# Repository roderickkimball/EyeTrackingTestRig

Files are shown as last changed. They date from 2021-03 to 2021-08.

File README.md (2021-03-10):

The Eye Tracker Test Rig is a robotic device that utilizes a set of artificial eyes and an artificial face to both manually and autonomously control a Surface Laptop via interface with a remote eye tracker. The rig features 3-axes of translational motion and 2-axes of rotational motion. The combination of these axes is intended to provide human-like motion for the artificial eyes and face. The rig is controlled via an Arduino Mega and features manual control via an Xbox controller.

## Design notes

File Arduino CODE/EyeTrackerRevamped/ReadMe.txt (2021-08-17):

State Machine Summary:

•	Menu Mode - Idle state of the robot. Waits for commands from the API or serial communication to switch states or return the current state.
•	Robot Run - Runs the robot by moving the desired subsystem to the commanded position. The commanded position is decoded from the g-code that is sent from the API. 
		ge(float, float) - moves eyes; gs(float, float, float) - moves shoulder; gn(float, float, float) - moves neck
•	Eye Calibrate - State to calibrate the eye servos. Calibration of the eye servos is important for all 4 eye servos to know what the 90-degree straight forward position of the eyes is. All commanded angles are incremented/decremented from this 90-degree position.
•	Neck Calibrate - State to calibrate the neck steppers. Calibration of the neck steppers is important to save the position of the steppers at which the neck platform is completely level with the base plate.
•	Shoulder Calibrate - State to calibrate the shoulder steppers. Calibration process includes the shoulder steppers hitting their "zero" or "home" position limit switches. 

Class Structure Summary:

ROBOT.h

•	Robot Class: Class encapsulates the entire eye tracker robot, including the eye, neck and shoulder objects, along with members indicating the current state of the robot, transformation matrices that go from the center 
		of the left and right eye to the screen, and public member functions to run the different states of the robot and interface with the API. 

	Private Members: 
		robotState (StateMachineState): Enumeration object that stores the current state of the robot (refer StateMachineState enumeration in Function.h).
		robotEyes (Eyes object): Eyes class object encapsulating the eye subsystem.
		robotNeck (NeckClass object): NeckClass object that encapsulates the neck subsystem.
		robotShoulder (Shoulder object): Shoulder object that encapsulates the shoulder subsystem.
		screenDotPos (Matrix(4)): Matrix that denotes the coordinates of the desired gaze position for the eyes.
	
	Protected Members:
		gLS, gRS (Matrix(4,4)): Matrices that denote the transformation matrix that goes from the center of left and right eyes respectively to the center of the screen.

	Private Member Functions:

		char getSerialCommand(): Obtains a single character command from the Hardware Serial or the connection to the API by performing Serial.read().
			Returns the passed in character from the serial port. 

		void updateKinematicChain(): Recalculates gLS and gRS by pulling the inverse transformation matrices from the shoulder, neck and eyes. Refer GetInverse****Transformation() in Eyes.h, RobotNeck.h and Shoulder.h.

		void setRobotPosition(char command): Sets the desired subsystem to the commanded position. This function is called immediately after the g code is sent from the API or serial communication, and is responsible for decoding the rest of the 
			g command to determine which subsystem is to be moved. 
	
		void getRobotPosition(char command): Gets the current position of the desired subsystem. This function is called immediately after the p command is sent from the API or serial communication, and is responsible for decoding the rest of the
			p command to determine which subsystem's position is to be printed.

		void runMenuModeState(): Runs the MenuMode state, that essentially waits for a user input from the Serial terminal to change the state to a desired one. 
			References getSerialCommand(). If the command is m, then it prints the current state. If the command is s-(int), it changes the state to the enumerated integer passed in.

		void runRobotRunState(): Runs the Robot Run state, that essentially reads the commands set in from the serial port or API, decodes the g or p code that is sent is and subsequently calls setRobotPosition(char) or getRobotPosition(char).
			'm' returns the state to MenuMode.

		void runEyeCalibrationState(): References getSerialCommand() and passes in the character obtained into Eyes::CalibrateEyes(char) function. 
			'm' returns the state to MenuMode.

		void runShoulderCalibrationState(): References the Shoulder::HomeShoulder() function that zeroes all three stepper axes. 'm' returns the state to MenuMode.

		void runNeckCalibrationState(): References getSerialCommand() and passes the obtained character into the RobotNeck::CalibrateNeck(char) function. 'm' returns the state to MenuMode.

	Public Member Functions:

		void init(): Initialization function for the robot class object. Initializes the eyes, neck and shoulder objects encapsulated. Calls the read-from-EEPROM function in each of the class objects. Calls the updateKinematicChain() function
			to load all of the variable updates into the kinematic chain instance. 

		void SetState(int stateNumber): Sets the state of the robot to the enumerated value of the stateNumber integer. 

		int GetState(): Gets the current state of the robot and returns the integer value of the enumeration.

		void RunState(): Determines the state of the robot through a switch-case and calls the private member function corresponding to that state of the robot. 

EYESUBSYSTEM.h : 
The Eye Subsystem header file includes all the enumeration, variables, and the Eye Subsystem class. Details of each can be found below.
•	Enumerations: 
		EyeMotor: Symbolic names for denoting which motor is being individually controlled and calibrated. Used in eye calibration. 

•	Eyes Class: Class encapsulates the entire eye subsystem of the robot, with objects for the 4 servo motors and functionalities to calibrate the eyes and parallax the eyes on the screen. 

	Private Members: 
		xServoL, zServoL, xServoR, zServoR (Servo): Servo objects for the LeftX, LeftZ, RightX and RightZ servo motors. 
		lXCenter, lZCenter, rXCenter, rZCenter (long int): Center positions in microseconds for each of the servo motors. 
		lXmicroSecondsPerDegree, lZmicroSecondsPerDegree, rXmicroSecondsPerDegree, rZmicroSecondsPerDegree (float): Denotes the number of microseconds required to move the left/right eye servos one degree.
	
	Protected Members:
		    /*
      		T - will be the frame of reference located at the center of the top of the neck.
      		D - will be the frame of reference at the center of the eye mechanisms,
      		with Z up, X to the right and Y along the axis of the straight 90-degree eyes
	      	L - will be the left eye's frame of reference with the origin at the center of rotation
	        and is aligned with the D frame when the 90-degree angle is commanded
	        R - will be the right eye's frame of reference with the origin at the center of rotation
	        and is aligned with D frame when the 90-degree angle is commanded
		    */
		gTD, gDL, gDR (Matrix(4,4): Transformation matrices that go from one frame of reference to another given above.
		gLT, gRT (Matrix(4,4)): Inverse transformation matrices that go from the center of the left and right eyes to the top of the neck.

	Private Member Functions:
		void parallax(Matrix(4) leftDotPos, Matrix(4) rightDotPos): Commands the left and right X,Z servo motors to the desired position on the screen indicated by parameters. 
			Parameters: leftDotPos indicates the desired gaze position in the left eye’s frame of reference. rightDotPos indicates the desired gaze position in the right eye’s frame of reference.

	Public Member Functions:
		void init(): Initializes eye class object. Must be called anytime the class object is created. Attaches servo objects to corresponding pins. Defaults value for center positions. Writes servos to corresponding center positions.
			Provides transformation matrices with starting values.

		void ParallaxEyesToPos(Matrix(4) screenDotPos, Matrix(4,4) gLS, Matrix(4,4) gRS): Creates the gaze position coordinates in the left and right eye’s frame of reference using the dotPosition and inverse transformation matrix parameters.
			Parameters: screenDotPos matrix denotes the coordinates of the desired gaze position in the screen’s frame of reference.
				gLS denotes the TF matrix that goes from center of left eye to the center of screen. gRS is the same but for the right eye.

		void CalibrateEyes(char eyeCalCommand,  Matrix(4,4) gLS, Matrix(4,4) gRS): The aim of the calibration function is to make the 2 eyes point to a single point at the center of the screen. This is done by incrementing/decrementing the center positions of each servo motor by 1 microsecond. 
			Parameters: eyeCalCommand will either pass in ‘u’ for increment, ‘d’ for decrement and corresponding EyeMotor enumeration for changing calibration motor.

		void WriteEyeCalibrationVariablesToProm(): Writes the center positions of each servo motor to the predetermined address in the EEPROM (refer PromAddress enumeration in Function.h).

		void ReadEyeCalibrationVariablesFromProm(): Reads the center positions of each servo motor from the predetermined address in the EEPROM and stores it in the center position members in the class object.

		Matrix(4,4) GetInverseLeftEyeTransformation(), GetInverseRightEyeTransformation(): Gets the inverse transformation matrices for the left and right eyes in the eye subsystem. Referenced by Robot::updateKinematicChain().

NECKCLASS.h : 
The Neck class header file includes all the enumerations, variables and the RobotNeck class. Details of each can be found below:

•	Enumerations: 
		NeckMotor: Symbolic names for denoting which neck stepper motor is being individually controlled. Used in neck calibration.

•	Global Variables: 
		float knowStepperPos: This is used as the default or zero stepper position for all neck motors when the neck is parallel to the base. 
		float spoolRadius: Radius of the spool on stepper shafts.
		float spoolCircumference: Circumference of the spool
		float mmPerRevs: Length of thread released in each stepper revolution.
		float stepsPerRev: Number of steps for neck steppers in one revolution.
		float mmPerStep: Length of thread released in one stepper step.
		float yawMicroSecondsPerDegree: number of microseconds required to rotate the yaw servo one degree.

•	Robot Neck Class: Class encapsulates the stepper and servo objects that make up the entire neck subsystem, along with the functionalities necessary to calibrate and rotate the neck to the desired angle. 

	Private Members: 
		frontStepper, backRightStepper, backLeftStepper (AccelStepper *): Stepper objects made using AccelStepper for the 3 stepper motors of the neck. 
		m3FrontStepper, m3BackRightStepper, m3BackLeftStepper (M3Stepper): Stepper objects made using M3Stepper class for the 3 stepper motors of the neck. Using this class gives greater precise control over the steppers and avoids the steppers from missing steps (was a problem with AccelStepper).
		neckServo (Servo): Servo object for the neck that induces the yaw rotation.
		neckServoCenter (long int): center position in microseconds for the neck servo object.
		lastPhiR, lastPhiS, lastPhiD (float): stores the angles that the neck was last commanded to. 		
		lSpring (float): the length of the spring in the middle of the neck. 

	Protected Members:
		    /*
	      C - will be the origin frame of reference located at the center of the Z-axis stage,
	      that the neck and eye mechanisms are mounted to.
	      Y - will be the frame of reference located at the center of the yaw rotation servo.
	      N - will be the frame of reference located at the base of the neck of the robot.
	      T - will be the frame of reference located at the center of the top of the neck.
		
		These frames of references are used solely to calculate the cable length that is required to move the neck to the commanded angles.
	       O - signifies the origin point of the neck at the middle of the base.
	       B1 - front point at the base; B2 - back right point at the base; B3 - back left point at the base;
	       P1 - front point at the top; P2 - back right point; P3 - back left point; PC - center point at the top
		    */
		gCY, gYN, gNT (Matrix(4,4): Denotes the TF matrices that go from one frame of reference to the other given above.
		gO_B1, gO_B2, gO_B3, gPC_P1, gPC_P2, gPC_P3 (Matrix(4,4)): """""""
		gB1_P1, gB2_P2, gB3_P3 (Matrix(4,4)): """"""""
		gTC (Matrix(4,4)): Denotes the complete inverse transformation matrix that goes from the top of the neck to center of z-axis stepper stage.
	
	Private Member Functions:
		void updateNeckTransformation(): Takes in the angles that the neck was commanded to and performs the computation of the cable length required from all 3 steppers to move the neck to the commanded angle. 

	Public Member Functions: 
		~RobotNeck(): Destructor function for the neck class object that deletes the pointer objects in the class.

		void init(): Initializes the three-neck stepper object, yaw servo object, sets maximum speed and acceleration for the stepper motors, and defaults the last stepper position and lSpring values. 

		void CalibrateNeck(char neckCalCommand): The aim of the calibration process is to level the neck so that it is parallel to the base of the neck. and 0.127m away from the base of the neck. This is done by incrementing/decrementing the current position of the steppers by 50 steps, individually to a point where it is level. 
			Parameters: neckCalCommand will either pass ‘u’ for incrementing, ‘d’ for decrementing, corresponding enumeration for NeckMotor to change the calibration motor or ‘z’ to save a hand-cranked position as the level position. 

		void MoveNeckManually(float PhiS, float PhiR, float Yaw): Commands the neck steppers to the desired angle given by the parameters. Saves the current positions of the steppers as the last steppers positions for corresponding stepper. Note: This function only sets the desired target location for the steppers. This function call must be followed by RunSteppers() function call.
			Parameters: PhiS – gives the direction of tilt. PhiR – gives the amplitude of tilt. Yaw – gives the desired angle of yaw. 
		
		void SetLastNeckPosition(): Sets the current positions for the neck steppers upon startup based on the last commanded neck angles.

		void RunSteppers(): Runs the steppers to the desired target location set prior to this function call.

		void WriteNeckPositionToProm(): Writes the last commanded neck angles variables for each stepper object to the predetermined address in the EEPROM (refer PromAddress enumeration in Function.h).

		void ReadNeckPositionFromProm(): Reads the last commanded neck angles variables from the EEPROM and sets the current positions for all stepper objects as their corresponding last stepper position variable. 

		Matrix(4,4) GetInverseNeckTransformation(): Returns the inverse neck transformation matrix that goes from the top of the neck to the center of z-axis stepper stage. Referenced by Robot::updateKinematicChain().
		
SHOULDER.h

•	Shoulder Class: Class encapsulates the stepper objects that makes up the shoulder of the robot, along with the functionalities necessary to home and move the shoulder to the desired position.

	Private Members: 
		xStepper, yStepper, zStepper (AccelStepper *): AccelStepper pointer objects for the X,Y and Z shoulder steppers. 
		stepsPerM (float): The number of steps required to move the steppers 1 meter. This value was experimentally determined and maybe subject to change depending upon the stepper motor being used. 

	Protected Members:
		    /*
	      S - will be the screen frame of reference with the zero coordinate at the center of the screen,
	      X will be to the right, Z up, and Y into the screen
	      B - will be the origin frame of reference with the zero coordinate at the position where the
	      stages of the 3-axis shoulder steppers hit the limit switches or zero position
	      C - will be the origin frame of reference located at the center of the Z-axis stage,
	      that the neck and eye mechanisms are mounted to.
		    */
		gBS, gBC (Matrix(4,4)): Transformation matrices that go from one frame of reference to another given above.
		gCS (Matrix(4,4)): Total inverse transformation matrix that goes from the center of z-axis stepper stage to the center of the screen. 

	Private Member Functions: 

		bool zeroStepperX(), zeroStepperY(), zeroStepperZ(): Homes the X,Y or Z axis stepper till the limit switch on the corresponding axis is tripped. Sets that position as the zero position of the corresponding axis stepper. 
			Returns true when the limit switch is tripped. 

		void updateShoulderPositions(): Updates the current positions of the shoulder steppers in the gBC transformation matrix. 

	Public Member Functions: 
		~Shoulder(): Destructor for the shoulder class object that deletes the AccelStepper pointer objects. 

		void init(): Initialization function for the shoulder class object that initializes the AccelStepper objects, sets maximum speed and acceleration for the individual steppers and defaults the value for stepsPerM. 

		bool HomeShoulder(): Homes the shoulder axis steppers to set their zero positions. Once all steppers have finished homing, it calls the updateShoulderPositions function to update TF matrix.
			Returns true when all steppers have finished homing.

		void MoveShoulderToPosition(float x, float y, float z): Moves the shoulder steppers to the desired X,Y,Z coordinates denoted by the parameters. Calls updateShoulderPosition() once the shoulders have moved to their final position.
			Parameters: the parameters denoting the desired position must be in meters with the home position as zero. 

		float GetShoulderPosition(char desiredStepper): Returns the current shoulder position of the stepper denoted by the character parameter.
			Parameters: desiredStepper must be 'x' for X, 'y' for Y and 'z' for Z axis stepper.

		void WriteShoulderPositionToProm(): Writes the current shoulder positions to the predetermined address in the EEPROM (refer PromAddress in Function.h for more details).

		void ReadShoulderPositionFromProm(): Reads the shoulder positions from the predetermined address in the EEPROM and sets the current positions of the steppers to the extracted values.

		Matrix(4,4) GetInverseShoulderTransformation(): Gets the total inverse transformation matrix for the shoulder subsystem. Referenced by Robot::updateKinematicChain().

M3STEPPER.H

•	M3Stepper Class: Class that encapsulates members of a stepper object, along with functions to move the stepper one step, set stepper speed, current position and target position.

	Private Members:
		_currentPosition (long): Denotes the current position of the stepper object.
		_targetPosition (long): Denotes the target position of the stepper object.
		_direction, _pulse (int): Denotes the direction and pulse pins of the stepper object.
		_speed (float): Denotes the current set speed of the stepper.

	Public Member functions:
		void init(int directionPin, int pulsePin): Initialization function for the stepper object. Sets the pin modes for the direction and pulse pins.
		
		void SetCurrentPosition(long stepPosition): Sets the current position of the stepper to the parameter passed in. 

		long CurrentPosition(): Gets the current position of the stepper.

		void SetSpeed(float desiredSpeed): Sets the desired speed for the stepper.

		float GetSpeed(): Gets the current speed of the stepper.

		bool IsReached(): Checks if the stepper has reached its target position.

		void MoveTo(long target): Sets the target position for the stepper.

		void RunStepper(): Pulses the stepper from low to high, producing one step in the desired direction.

KINEMATICCHAIN.h

•	Kinematic Chain Class: Class that encapsulates all the static functions that are used to create and manipulate the transformation matrices.
	
	Public Member Functions:
		Kinematic Chain(): Constructor of the instance of the class. This is a private member function because it should only be instantiated once throughout
					the execution of the code. The function populates the transformation matrices with default values.

	Static Public Member functions:
		Matrix(3,3) eye(): Creates a 3x3 identity matrix.

		Matrix(3,3) hat(): Function to find the matrix projection of a given 3x1 matrix.

		float norm(Matrix(3) v): Normalizes a given 3x1 matrix. This is done by finding the square root of the inner product of the parameter vector with itself.

		Matrix(3,3) rodrigues(Matrix(3) xI): Function to obtain the projection of an identity matrix about the given axis of rotation passed in as parameter.

		Matrix(4,4) expmXI(Matrix(6) xI): Function to calculate the matrix exponential of the given rotational/translation vector. This function is meant to return the transformation matrix
							given that we provide the rotational and translation values from one reference frame to another.

		Matrix(3,3) OuterProduct(Matrix(3) w): Returns the result of performing outer product.

		Matrix(3) CrossProduct(Matrix(3) w, Matrix(3) v): Returns the result of performing cross product.

		Matrix(4,4) xForm(float alpha, float beta, float gamma, float x, float y, float z): Creates the transformation matrix, given the rotation and translation values.

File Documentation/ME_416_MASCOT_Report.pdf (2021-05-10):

ME 416: Senior Design

Spring 2021

Quantitative analysis of Eye tracker testing rig

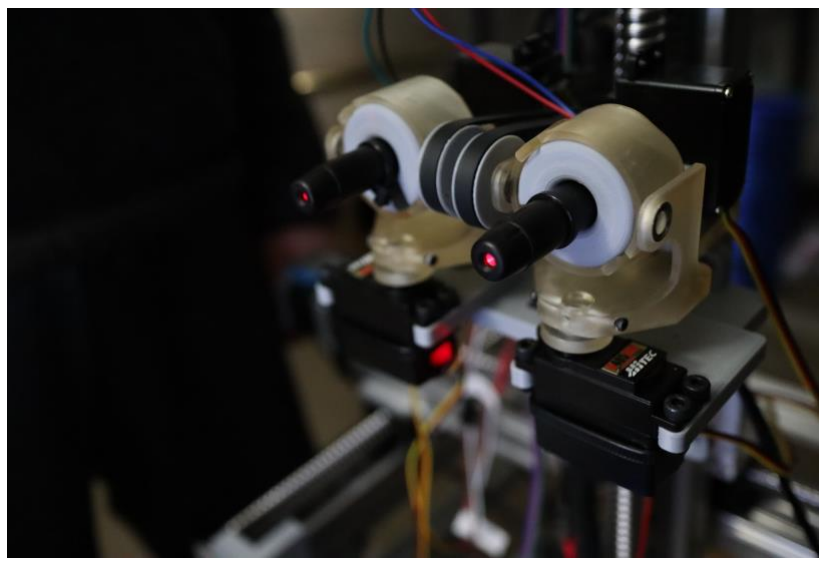
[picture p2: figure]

Brenno Aguiar Bonfim Cruz

Chenhao Yu

George Sam Eralil

Kyle Butzerin

Mathew Ubachs

Matthew James

Date of Submission: 04/29/2021

Figure 1 – Eye Subsystem of testing rig

1. Introduction

Amyotrophic Lateral Sclerosis (ALS) is a progressive neurodegenerative disease that destroys a patient’s nerve cells in the brain and spinal cord. Consequently, it takes away the patient’s ability to control motor functions including speaking, writing, and eventually breathing. Despite being classified as a rare disease, roughly 140,000 patients worldwide every year are diagnosed with ALS. This is equivalent to almost 384 new cases every day (International Alliance of ALS/MND Associations n.d.).

Although a decline of motor functions like moving and speaking is characteristic of ALS, studies have found a resistance of sphincter and sensory functions, as well as oculomotor functions (Proudfoot et al., 2015). Therefore, eye tracking systems have proved to be a great resource for ALS patients as they provide the ability to speak and write by controlling a PC using their eyes. However, studies note that most eye tracker systems only work under specific constraints, like a specific angle or spatial location of the user’s head or the user’s age
(Dalrymple et al., 2018). This can seriously limit the options available to a consumer and oftentimes the user may be oblivious to these requirements at the time of purchase.

For our capstone project, we are building an eye tracker testing rig that will provide a means to collect data on a manufacturer’s eye tracker and standardize the testing procedure for eye trackers. The testing rig can also be used to produce benchmarks for eye trackers from different manufacturers.

The eye tracker testing rig that we developed consists of three major subsystems: the eyes, the shoulder or gantry, and the screen subsystem. The eye subsystem consists of 2 individually actuated eyes that use 2 servos each, to control the pitch and yaw rotations of the eyes. A “parallax” function developed in Arduino enables the eyes to focus on a single point on the screen continuously. The gantry subsystem simulates a human shoulder and is actuated by 3 stepper motors, that can move the face or the eyes in the X, Y and Z axes. The screen subsystem consists of a Microsoft Surface tablet mounted with a Tobii eye tracker, which will be used to move a cursor on the PC using the eyes.

The objective of this experiment is to characterize the performance of our eye tracker testing rig by allowing it to type a predetermined message on the PC using a virtual keyboard. The process of typing out the message will be repeated at different shoulder positions to find the most optimal positional parameters that provide the best performance metrics. The performance metric we will be using is the accuracy rate obtained by determining the number of characters at their respective positions in a sentence that the robot got correct.

2. Literature Review

This section details a brief literature survey on the research efforts that have been conducted to measure the precision of eye-trackers. We describe what has been found on the underlying principle of eye trackers from Tobii and the necessary parameters required to interact with them.

The survey also attempts to identify the best parameters for the experiment based on work that has been previously done in the field of eye tracker analysis. Finally, we reflect on the information gap that currently exists in the field that will define the need for our experimentation.

Tobii eye tracker systems primarily rely
on three main face parameters to obtain a
precise location of where we are looking on a screen. These include, the face geometry, the eye location on the face and the pupil location. The exact coordinates of gaze on a screen are determined by using bright and dark pupil tracking (Tobii n.d.) performed using an array of infrared lasers.

Wang et. al. in their study of artificial
eyes (AEs) for precision measurement of
eye-trackers, use AEs from different

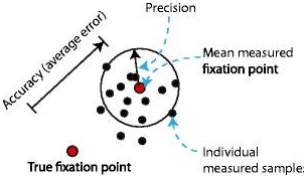
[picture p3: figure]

manufacturers and determine the accuracy and precision of eye trackers. The authors note that spatial accuracy and precision are the most important performance metrics for eye data quality. The authors define accuracy as the difference between the actual gaze position and the gaze position estimated by the tracker, and precision as the repeated reliability to produce a given measurement of the eyes (Wang et. al, 2017). The authors found that when ranking the precision scores of AEs with human data, eye trackers with higher sample rates like the SMI HiSpeed and the EyeLink came out in the first four places, while the ones with lower sample rates like TobiiX2 and EyeTribe were ranked at the bottom.

In the comparison between the different AEs, it was noted that the OEMI-7 AE could be tracked by all the eye trackers. However, the authors go on to note that the OEMI-7 has a 7-mm pupil, whereas human pupil sizes range from 2 to 8mm. Wang et. al. propose that this could be a potential source of imprecision for the eye-trackers (Wang et. al., 2017). Since the authors obtained the best results with the OEMI-7, this will be the AEs that will be used in our experimentation. However, it would remain to be noted what effects an improved AE could have on the accuracy of our results.

In another study conducted on the influence of eye physiology on eye-tracking data quality, it was found that blue eyes performed poorly in comparison to brown eyes (Nystrom et al., 2013). The authors also found a similar decay in precision among participants who wore glasses when compared to uncorrected eyes. Therefore, brown unobstructed eyes will be used in our experimentation as well to minimize bias errors.

In the same study, Nystrom et. al. also note that eye tracker precision can be increased by increasing the pixel resolution at the eye by moving the eye trackers closer. However, being limited by the large pupil size of OEMI-7 AEs and uncertainties regarding the working range for

Figure 2 Accuracy vs Precision for eye trackers. Created by Wang et. al, 2017 the Tobii eye tracker, we do not quantitatively know the relationship between spatial position of the eyes and precision of the eye tracker. This would be the information gap that currently exists and hence defines the need for this experimentation.

3. Theory

As mentioned previously, our primary goal is to obtain a performance metric of our robot’s interaction with the Tobii eye tracker. To achieve this goal, we used a mathematical concept called kinematic chain. This mathematical tool is widely use in robotic applications. In simple words, this mathematical tool allows for representation of joints of a robot in matrix form. This matrix contains the rotation and translation associated to that joint. Each one of these matrices are called frames of reference. (MARK W. SPONG 2020)

Every element is called Frame of Reference (FOR), which is essentially a matrix containing rotation denoted by “R” and translation, denoted by “T” as shown below.

g = [

R T
0 1

]

We can link two joints of a moving robot by using what is called transformation matrix. This transformation matrix is the result of rotation and translation from one frame of reference to another. For instance, let us take a matrix gij, where “i” and “j” are points in 3D space. The gij matrix represents a transformation from the point “i” to the point “j”.

For systems with no rotation, the “R” portion of the matrix is equivalent to a three-by-three identity matrix.

R = [

1 0 0
0 1 0
0 0 1

]

The translation portion of a gij matrix, indicates the translations in x, y, and z from “i” to “j”.

T = [

x
y
z

]

Now that we understand how the joints are linked, we can extrapolate this concept to our application.

First, we must identify all “joints” in our robot. To address every joint in this system, we will subdivide the robot in five elements: base, stage, eye mount, left eye, and right eye (Table 1, Fig. 4 and 5).

Naming Convention for Frames of Reference

B | Base situated on the chassis of the robot
C | Center of the stage sitting on the power screw
D | Imaginary point between the eyes

R | Center of the right eye
L | Center of the left eye
S | Screen
Table 1 – Naming Convention for Frames of Reference

Our objective here is to use the kinematic chain to obtain the coordinates and rotations of each one of the eyes, hence finding the input our eye servos need.

The transformation matrix from the eyes (L&R) to the screen (S) is given by the following matrix multiplication:

gLS = [(gLD)

−1
(gCD)

−1
(gBC)

−1gBS] Ps (1)

gRS = [(gRD)

−1
(gCD)

−1
(gBC)

−1gBS]Ps (2)

Where Ps is the target position on the screen; gLS and gRS matrices correspond to the location and orientation of the left and right eye with respect to the screen.

The final step is to convert these coordinates in angles using four-quadrant inverse tangent. This method returns angles that have their signs tied to the quadrant at which the point is at. For instance, if our point is on the first quadrant, the cosine and sine are positive.

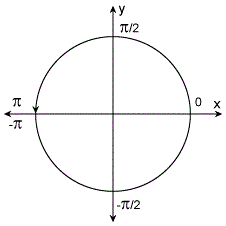
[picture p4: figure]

Figure 3 – Four-quadrant inverse tangent representation (MATLAB n.d.)

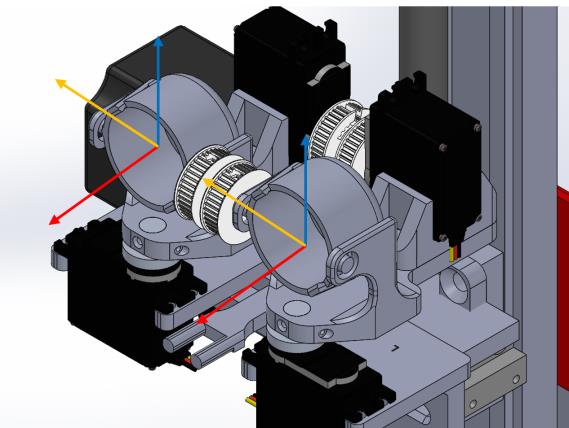
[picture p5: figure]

Figure 4 –"R" and "L" frames of reference

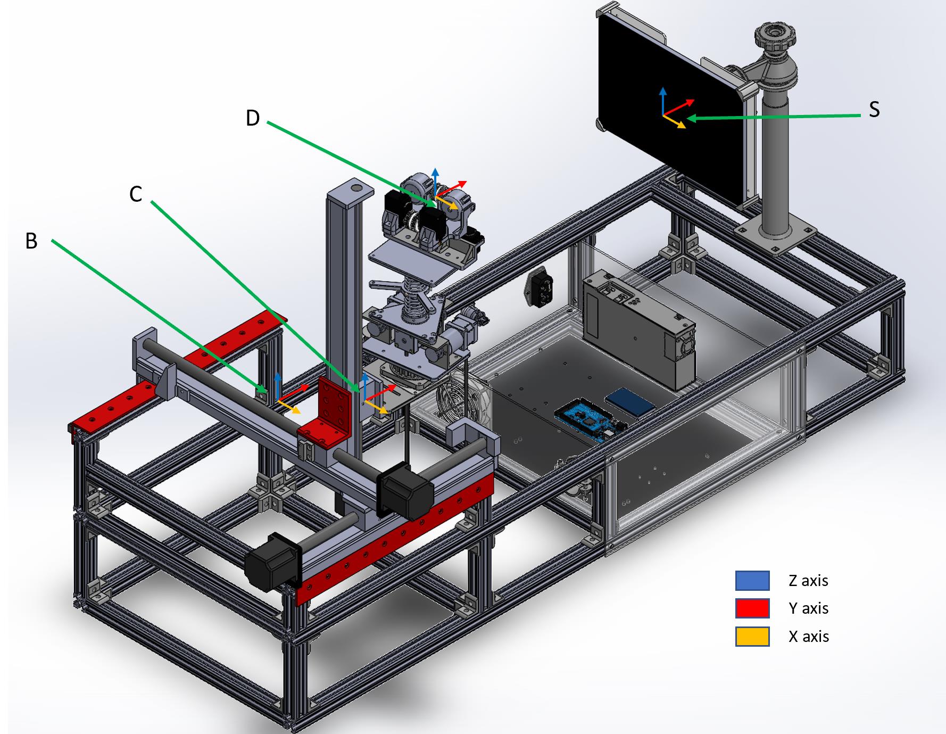
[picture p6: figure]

Figure 5 - “B”, “C”, “D”, and “S” frames of reference.

4 Experiment

4.1 Experimental Setup

Our experimental setup consists of three subsystems. 1) Eyes and mounts, 2) Gantry, 3) screen and Tobii. The eye subsystem is composed of four servos, a pair of lasers, and a pair of eyes. The gantry is composed of three steppers with their respective stages and power screws. The third subsystem consist of a Microsoft Surface and the Tobii eye tracker.

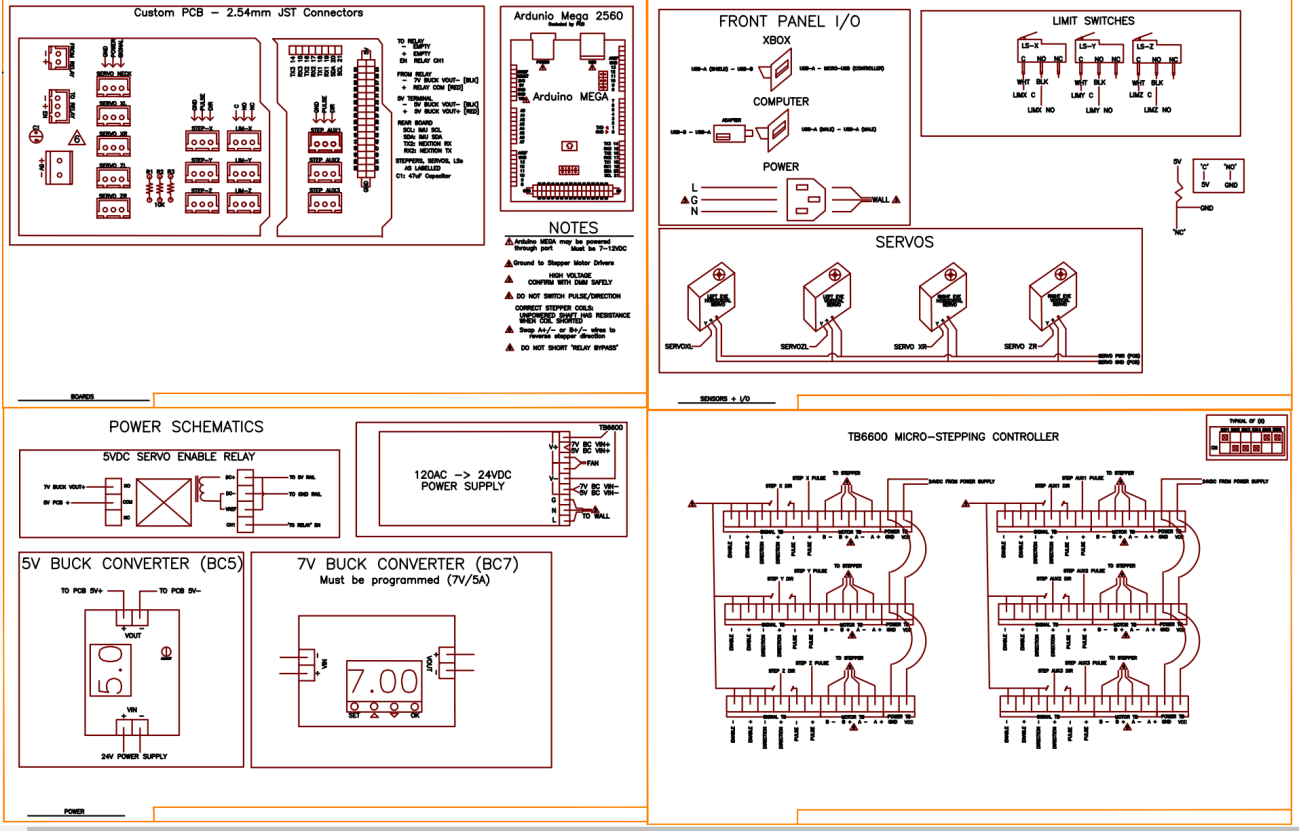
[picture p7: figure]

Figure 6 – Microsoft Eye tracker Wiring Diagram.

The eye subsystem relies on four servos to control the pitch and yaw for each one of the eyes. We are using micro lasers embedded in a cap that slides over the eyes as seen in Fig. 7. The lasers are solely used for calibration purposes. They should be stowed after calibration. The gantry subsystem is responsible for the translation of the eye mechanism in x, y, and z. These two subsystems are being controlled using an Arduino Mega, a USB Shield, and stepper drives. Finally, we have the screen subsystem. This subsystem will be treated as a black box throughout the paper due to restricted access to proprietary technology.

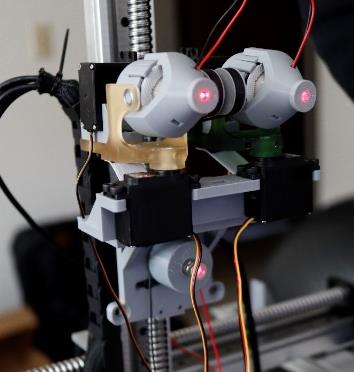
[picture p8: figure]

Figure 7 – Eye Subsystem

Before we started testing, we had to assure our system was calibrated. We used the wallpaper shown on the center to calibrate the eye convergence by sending both eye lasers to the blue dot at the center of the wallpaper. We also used the same wallpaper to cross-check the gantry positioning. Next step was to calibrate the eyes using the Tobii eye tracker. Finally, we were ready to make our robot start typing.

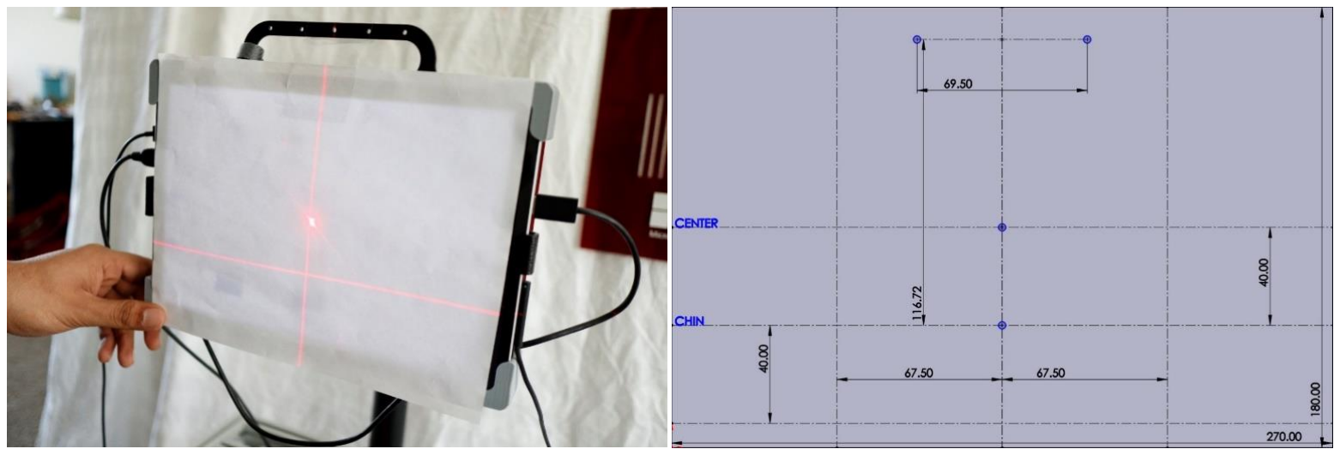
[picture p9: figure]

Figure 8 – Laser calibration (left picture) and wallpaper used for calibration (right picture).

The testing strategy was simple. We intend to test how the system can perform at different positions. To achieve that goal, we pre-determined six different locations to perform the test (Fig. 9). Each test would take approximately eight minutes. We essentially made our robot type the same sentence at each location. The sentence came from Steve Gleason, here is the sentence:

“Life is difficult. Not just for me or other ALS patients. Life is difficult for everyone. Finding ways to make life meaningful and purposeful and rewarding, doing the activities that you love and spending time with the people that you love, I think that is the meaning of this human experience.” – Steve Gleason

We picked this sentence because besides resonating with the project, it has a wide range of letters that can challenge the robot. The total number of characters is 294.

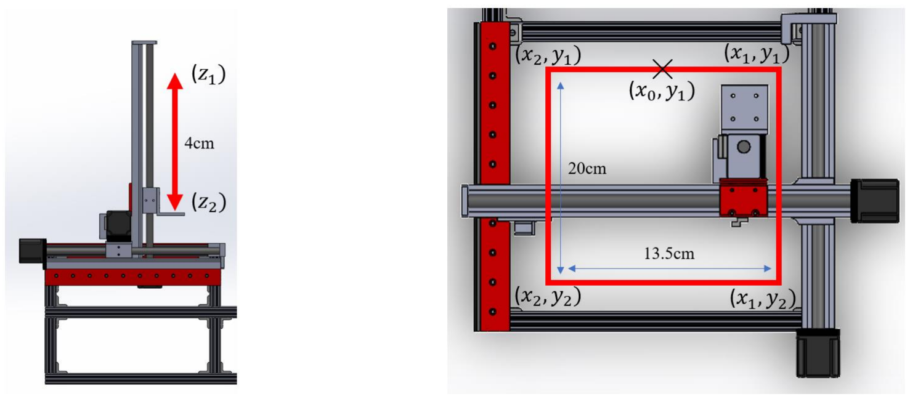
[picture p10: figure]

Figure 9 – Schematic of pre-determined locations used for testing.

4.2 Experimental Procedure

Start-Up Procedure:

1. Before beginning the experiment, make sure the robot is plugged onto 120 AC.
2. Make sure the screen is centered and it is positioned vertically.
3. Turn the Microsoft Surface on.
4. Insert the Tobii eye tracker onto the slots right below the Microsoft Surface. There are two magnets that can assure the Tobii is in place.
5. Turn the power supply on and plug in the Xbox controller using the USB cord.
6. Insert the laser caps onto the eyes until it clicks and plug the red and black cables to live and neutral female pins.
7. Press “Y” on the Xbox controller. This will initiate the stepper calibration sequence. Please wait until the robot stops moving.
8. Press “A” on the Xbox controller. This will initiate servo calibration sequence.
9. Open the calibration wallpaper located in the PowerPoint presentation on the desktop.
10. Move both laser points to the blue dot located on the center of the screen. Use the left and right arrows from the D-Pad to switch between the servo motors. Use the Up and down arrows to move the servos. Press “L1” to exit and save calibration.
11. Remove the laser caps.
12. Open Tobii Calibration and make sure the software can see the eyes.
13. Press “L2” on the Xbox to initiate Tobii eye calibration.
14. There are four calibration points. As soon as Tobii recognizes the first point, press “B” to move to the next one.
15. Press “L1” on the Xbox controller to initiate servo manual mode.
16. Press “R3” to initiate the testing.

Data Acquisition:

1. Press “R1” to enter stepper manual mode.
2. Move to the pre-determined positions using the analog stick.
3. Press “R3” to enter testing mode.
4. Repeat the operation for the other preset values.

Shut-Down Procedure:

1. Turn the power switch off.
2. Unplug the power cord out of the outlet.

### 3. Turn the Microsoft Surface off

4.3 Data Analysis & Uncertainty

After collecting the word output from our experiment, we calculated the success rate per sentence during every test. This calculation was performed by simply dividing the number of characters missed by the total number of characters. We plotted the success rate versus gantry position as we can see in Fig. X.

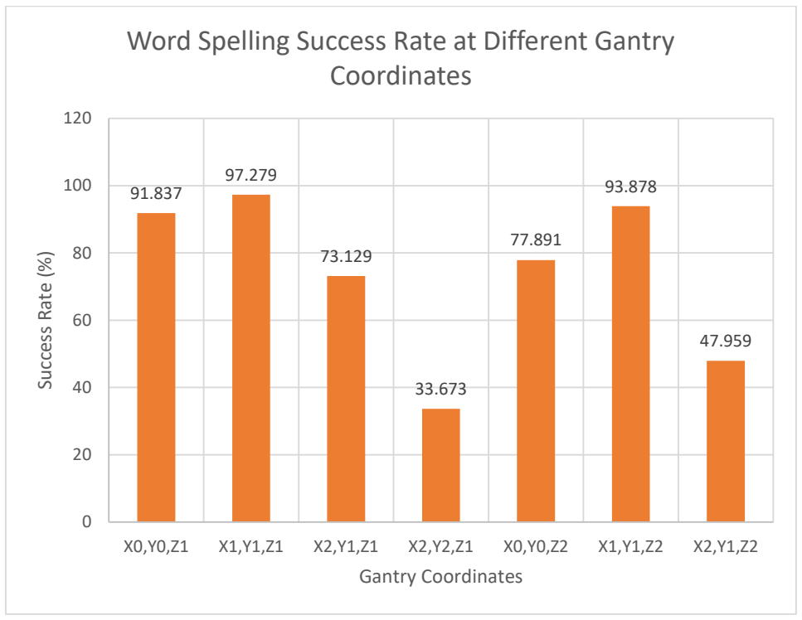
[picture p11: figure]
Success Rate (%); Gantry Coordinates; Coordinates

Figure 10 – Word Spelling Success Rate at Different Gantry Coordinates

### Word Spelling Success Rate at Different Gantry

5 Results and Recommendations

The best result was found at coordinate (X1, Y1, Z1) which corresponds to the front right side of the screen. At this location, the experiment had a 97.28% success rate. The second best was at (X0, Y1, Z1) which corresponds to front and center of the screen; the success rate was of 93.88%. The lowest accuracy was obtained at (X2, Y2, Z1) at the back and left side of the screen; the success rate was of 33.67%

The results deviated slightly from our predictions. Initially we thought that the robot would perform the best at the center position, which was not the case. The best result was obtained at the right side of the screen instead. This led us to believe that there is a gap in understanding on how the Tobii works. As mentioned previously, the eye tracker is a black box, thus we do not know if the problem lies on our robot or the eye tracker.

We would like future groups to carry out this research and investigate the theory behind machine vision technologies used by eye trackers. We intend to use this information to understand the engineering requirements necessary to make the testing rig as unbiased and realistic as possible, and not to bypass the system.

Furthermore, more work needs to be done to expand on the testing procedure that we have developed. Future work would focus on expanding the testing region to cover the entire screen and use metrics like accuracy and precision mentioned before to analyze the system. Moreover, testing of different eye tracker systems and different/custom built AEs would be beneficial to identify the true sources of uncertainties in the testing.

## Bibliography

Anna Maria Feit1, 2 Shane Williams2 Arturo Toledo2,3 Ann Paradiso2. 2017. Toward Everyday Gaze Input: Accuracy and Precision of Eye Tracking and Implications for Design. Research Paper, Microsoft Research.

n.d. International Alliance of ALS/MND Associations. Accessed 03 29, 2021. https://www.alsmndalliance.org/what-is-alsmnd/.

MARK W. SPONG, SETH HUTCHINSON. 2020. Robot Modeling and Control. Hoboken: John Wiley & Sons, Ltd.

MATLAB. n.d. MathWorks. Accessed April 25, 2021. https://www.mathworks.com/help/matlab/ref/atan2.html.

Nystrom, M., R Andersson, K Holmqvist, and J van de Weijer. 2013. "The influence of calibration method and eye physiology on eyetracking data quality." Behavior Research Methods.

Proudfoot, Malcolm, Ricarda A.L. Menke, Rakesh Sharma, Claire M. Berna, Stephen L. Hicks, Christopher Kennard, Kevin Talbot, and Martin R. Turner. 2015. "Eye-tracking in amyotrophic lateral sclerosis: A longitudinal study of saccadic and cognitive tasks." Amyotroph Lateral Scler Frontotemporal Degener.

Tobii. n.d. Tobii Dynavox. Accessed 03 25, 2021. https://www.tobiidynavox.com/about/about-us/how-eye-tracking-works/.

Wang, Dong, Fiona B. Mulvey, Jeff B. Pelz, and Kenneth Holmqvist. 2017. "A study of artificial eyes for the measurement of precision in eye-trackers." Behavior Research Methods.

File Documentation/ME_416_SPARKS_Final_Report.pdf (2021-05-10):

# Eye Tracker Robot: Test Rig with Integrated Neck

### Sponsored by:

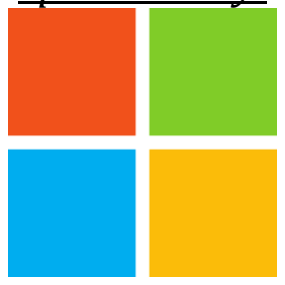
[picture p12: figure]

### Microsoft Corporation Redmond, WA 98052

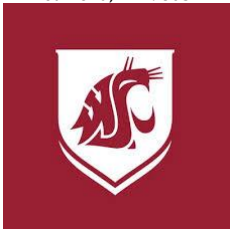
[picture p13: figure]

### Brittney Downing, Carson Kreager, Max Larsen, Kaitlyn Lewis, Bennett Moore

### Department of Mechanical and Materials Engineering Washington State University Pullman, WA 99163

### Executive Summary

The first goal of our project was to build and deliver by March 1st

, a replica robot based on the original one designed during the fall semester of 2020. The second goal was to design a neck that could be retrofit onto the robot to add an additional three degrees of motion and allow for more indepth eye tracker testing. For our neck retrofit, the two designs that we considered were a 3 degree of motion (DOM) Stewart platform, and a spring-cable neck design. After consideration of both, the spring-cable neck design was chosen as it would be shorter and more stable than a Stewart platform. After going through multiple design iterations, we finalized a design that offered even more flexibility than a human neck and could easily be integrated into existing robots. Electrically many improvements and modifications were made, including but not limited to, implementing a custom PCB, adding additional TB6600 micro-stepper controllers, and improving cable management by increasing the electrical box size. Using transformation matrices to calculate the desired cable lengths, the stepper motors can tighten and loosen the cables to achieve the desired pitch and roll.

## Table of Contents

Executive Summary | 2
Introduction | 4
Results and Discussion | 4
Conclusions and Future Work | 8

### Introduction

This document outlines the goals and requirements for the completion of the eye tracker testing prototype. Eye trackers are used by people living with ALS or other neuro-physical disorders. With multiple eye tracker manufacturers and their inherently different designs, an eye tracker testing prototype is a necessity to establish an eye tracking quality industry standard.
The first goal of this project was to create a replica of the eye tracker testing robot to be delivered to Microsoft’s Redmond campus. Each of the two teams made a replica rig to get a total of three robots. Some changes were made to the robot such as adding a buck converter to allow the Arduino to be powered internally and changing the base box from wooden 2x6 to 8020 aluminum. These changes were based on issues identified in the previous semesters design during our replica construction process. As well as creating two more robots, the original Fall 2020 robot was also upgraded to use the same hardware as the spring 2021 replica robots, to then give three identical robots. This ensured a smooth integration of our hardware and software changes onto all robots and will make future work on these rigs much easier.
Our second goal was to create a neck upgrade for the Fall 2020 baseline testing rig to aid in the realism of the eye tracker testing as it relates to real-life patients. Our goal was to design a neck that is capable of around eighty percent of what an actual human neck can do and deliver a retrofit kit to Microsoft so they can incorporate this newly designed system into their robot. It was imperative that the new neck system could operate around three degrees of freedom to simulate neck muscle atrophy and Dropped Head Syndrome, which is a common result of living with ALS. The results from this neck upgrade to the baseline testing rig, and the data it provides will allow for the improvement of eye trackers. This is important because customers will have access to eye trackers that are more reliable for unique costumer conditions. Our neck upgrade for the baseline testing rig will allow us to test eye trackers when the head is not perfectly straight on.

### Results and Discussion

We considered two different neck designs when beginning our prototyping phase. One neck we were considering was a 3 degree of motion (DOM) Stewart platform, and the other was a spring and cable neck design. The Stewart platform was considered as it is a well-known design that is used in hundreds of different applications, especially in the aerospace industry for various simulators. Additionally, our concept would allow for up to thirty degrees of rotation in any direction. There was however concern with this design as u-joints tend to get stuck at their
angular extremes and the coding
required for this design would be
very complex. The spring and cable neck design was also considered due to its increased
flexibility | over | the | Stewart
platform, as well as its compact and human like design. We
decided to use the spring and cable design in the end because it would be more stable than the Stewart platform, and the issue with the u-

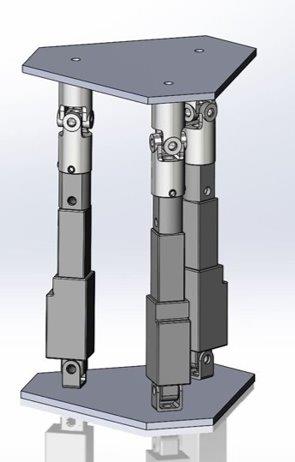
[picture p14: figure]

joints was nonexistent with this design. There are still issues that we are worried about with this spring cable neck design.

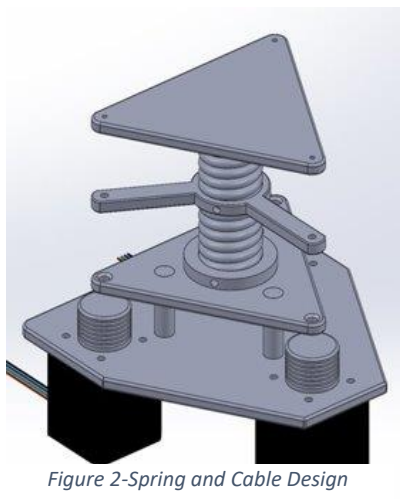
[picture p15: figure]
Figure 2-Spring and Cable Design

Figure 1-3 DOM Stewart Platform

For one, we do not know how well this spring will perform over time and after many uses. We believe that the spring could potentially plastically deform causing the neck to become inaccurate to the point that it could not be used and would need to be replaced. We are also worried about deformation in the cables connecting the stepper motors to the actuating platform. These cables could be stretched out over time such that they may eventually not be able to hold the load of the neck and will break.
After deciding to use the spring and cable design, the next step was to identify issues with our first iteration. None of our original designs took into consideration how the yaw should be incorporated into the neck. We decided to use belt driven timing pulleys that use a servo to control the yaw. The entire neck mechanism is mounted on top of the yaw mechanism such that the entire neck rotates. Additionally, our spring and cable design needed to be adjusted such that the rotational axis of the spindle attached to the stepper motors was perpendicular to the cable rather than parallel. These were the major changes from our initial design to our final design. However, many small, functional improvements were also made to the design. These include such things as the use of an incorporated z-bar structure into the neck for the steppers, a turntable for the yaw as opposed to the original slew bearing, and an integrated spring end for the bottom and top plates. These changes along with our final design are shown below.

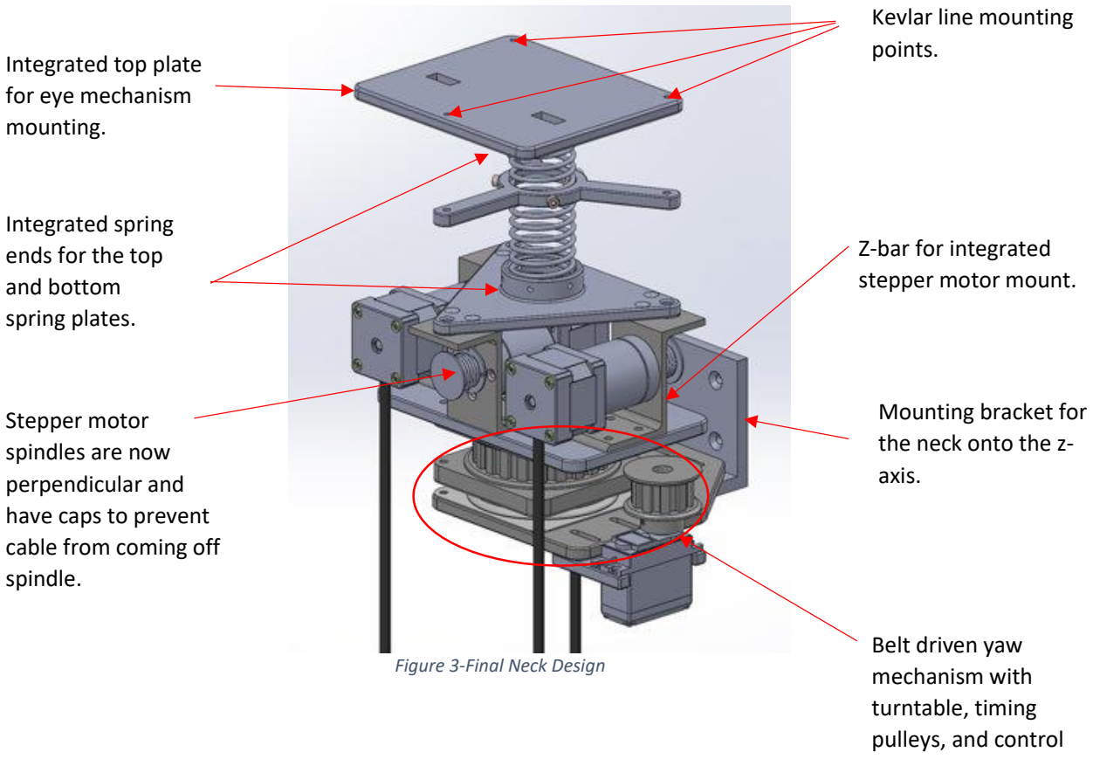
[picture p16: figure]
Figure 3-Final Neck Design; Belt driven yaw mechanism with turntable, timing pulleys, and control; Z-bar for integrated stepper motor mount.; Stepper motor spindles are now perpendicular and have caps to prevent cable from coming off spindle.; Integrated top plate for eye mechanism mounting.; Integrated spring ends for the top and bottom spring plates.; Mounting bracket for the neck onto the z- axis.; Kevlar line mounting points.

servo.

Our final neck design made use of three NEMA 14 stepper motors with universal gearboxes, as well as a 270 degree, 20kg-cm servo motor. Where the servo motor controls the yaw rotation of the neck using timing pulleys and a belt, the three stepper motors control the pitch and roll of the neck. Each stepper motor has a spindle that rotates to allow tightening or loosening of a Kevlar line at each of three points on the top spring plate. By combining the rotation of each of these stepper motors, we can achieve any combination of pitch and roll of our neck platform. Upon adding in the servo-controlled yaw system, it becomes possible to achieve any combination of pitch, roll, and yaw like what you would have in a human neck.
To manufacture this, all standard hardware like the motors, timing pulleys, turntable, screws etc. were ordered and are reflected in our bill of materials. Due to the required stiffness of the neck mechanisms, and strength needed to support the neck’s weight, it was decided that all plates except for the top and bottom spring plates should be machined out of a quarter inch aluminum plate. The mounting bracket was made form a standard ninety-degree extrusion, and the z-bar stepper mounting brackets were cut and machined from an aluminum z-bar extrusion. All other components like the spindles, spring plates, and various mounts were 3D printed using a standard FDM style 3D printer.
Coinciding to the mechanical aspect of this project was an electrical element. The original Fall 2020 robot had a few electrical troubles that needed to be addressed. One enhancement was a custom-made PCB board that was requested by Microsoft to help organize wiring and allow for a more reliable wire connection to the Arduino. The Fall 2020 team had plugged in terminal blocks into the Arduino itself, but they kept popping out on their own and did not make a solid connection which made the robot unreliable. Another feature the previous Fall 2020 team attempted was to internally power the Arduino Mega/PCB by utilizing a separate 5-volt power supply. A separate power supply was used because the 24-volt power supply was too powerful. Unfortunately, this did not work and to combat this issue the Spring 2021 teams decided to run power from the 24-volt power supply to the PCB but have a buck converter in-between to scale down the voltage to the 5 volts that was needed. This enhancement also allowed for the 5-volt power supply to be removed from the robot completely. Another improvement that was made was adding a buck converter between the 24-volt power supply and the eye servos. The Fall 2020 robot had some eye servo twitching when we got it and that made parallaxing extremely hard. The correction for this was simple, all that was required was a 7-volt buck converter that helped damp any noise in the power that the servos were receiving. Besides just fixing problems that the Fall 2020 robot had when received at the beginning of the semester, electrical modifications had to be made to accommodate the new neck components. Our team ended up making the electrical box 6 inches wider than the original Fall 2020 robot had. This was necessary to not only fit the two new buck converters, but also to fit the 3 additional TB6600 micro-stepping controllers that control the pitch and roll of the neck. Another new component added was an LCD screen that allows the user to interact with the neck without having to constantly update the code. Using the LCD screen, we also can see the angle at which the neck is located. To accomplish this an IMU was installed to give real time angle feedback of the neck location at any point in time. Throughout the Spring 2021 semester, our team went through three iterations of electrical box layout before deciding on the final box design. But due to these iterations, wire management has improved significantly. Another cause for improved wire management was the use of stranded and bell core wire. The Fall 2020 team attempted to chain together a lot of premade jumper wires that are commonly used in mechatronics kits because they’re convenient to plug into an Arduino board. But by doing this, the wire management looked unpleasing to the eye and was not as reliable as using normal stranded or bell core wire.
We went through 4 to 5 different methodologies for coding the neck. After talking with Dr. Swensen we decided to use transformation matrix math to calculate the transformation between the bottom and top plate. This in turn allowed us to calculate the desired cable length from a desired direction of tilt and amplitude of that tilt.

### Conclusions and Future Work

We can conclude based on our work that our neck will offer a little over one hundred percent of the flexibility that a real human neck can achieve and should be sufficient to test eye trackers. However, there are several issues which should be addressed during any future work done on this robot. One issue we are seeing currently in the hardware is that our neck is too heavy for the robot. This applies a torsional load to the linear axes of the robot and causes inaccuracies in our actual neck position. Weight reduction in the neck and reinforcement in the axes would mitigate this issue and would allow the neck to be more positionally accurate.
For the electrical element of this project, the biggest recommendation would be to replace the current PCB with a new one. The current PCB has a few issues and really needs to be remade to fix some of the fundamental issues. The first issue with the current PCB is that it uses digital pin 50 for one of the neck TB6600 micro-stepping controllers. This didn’t seem like a big problem until we realized that digital pin 50 is a special communication pin that always pulses high and low to attempt to find a communication signal. This means that no matter how we code it, that pin always pulses which makes the stepper motor pulse erratically. There is a coding fix to make that pin a regular digital pin, but every attempt made has not been successful. Plus, trying to fix a hardware problem with code is not the easier option.
Additionally, the traces on the PCB should be made larger. There have been a few servo related issues and it seems that maybe the traces on the PCB are to blame. So, if the PCB needs to be remade anyways to fix the digital pin 50 problem, then might as well just make the traces larger to prevent any possible overloading down the road. The last electrical improvement that is recommended would be to make the electrical box even bigger. The six TB6600 micro-stepper controllers are a bit cramped where they’re currently placed and there is room to make the box bigger. Plus, A larger box would be nice for future teams in case they need to add electrical components or move things around.
The elegancy of the neck control movement needs to be improved. The most up to date code is very accurate in calculating the transformation matrix but has not had enough time to iron out all the control bugs. The gains and limits need to be tweaked for smoother control.

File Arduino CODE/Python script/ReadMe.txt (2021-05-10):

Mascot_testing.py will generate X and Z coordinates for any message that is passed into it. 
The desired string message must be typed into the "message" variable in the script.
The script uses Eyetracker_Keyboard.csv file, which contains the coordinates for all the keyboard letters.
If the keyboard coordinate values change from the ones given in the .csv file, then these should be updated using the find_coordinates state of the robot. This state of the robot will provide you with the coordinates of gaze of the robot.

The python script will write the coordinate data to a GFG.csv file. 
The coordinate values will need to be copied from this .csv file and pasted into the autoCoordinates variable inside the arduino code.

HAPPY TYPING!

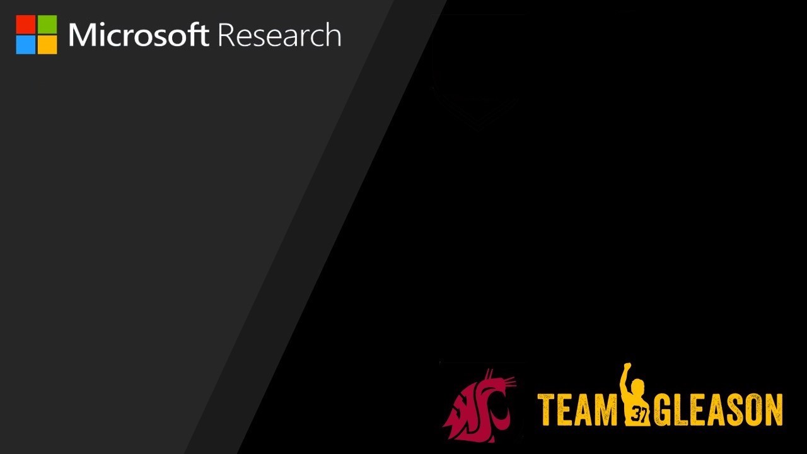
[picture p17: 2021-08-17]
EyeRobotControlApp/WSU_Gleason.jpg

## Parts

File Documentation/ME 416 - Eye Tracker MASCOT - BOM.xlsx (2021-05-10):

Item Name | Vendor | Catalog # | Qty | Unit Size | URL | Unit Price | Total Price
Quarton Red Dot Tiny Laser Module VLM-650-21 LPA (Mini-Size: Dimensions- D4 x 15 mm, Plastic Lens) | Amazon | NA | 2 | 1 | ="https://www.amazon.com/dp/B01KUSUBIM" | 30 | 60
Arduino Mega | Amazon | NA | 1 | 1 | ="https://www.amazon.com/ELEGOO-ATmega2560-ATMEGA16U2-Projects-Compliant/dp/B01H4ZLZLQ" | 16.86 | 16.86
Nextion Display 7" NX8048T070 Resistive Touch Screen UART HMI LCD Module 800x480 for Arduino Raspberry Pi | Amazon | NA | 1 | 1 | ="https://www.amazon.com/Nextion-NX8048T070-Display-Arduino-Raspberry/dp/B07QWPNW91" | 89.76 | 89.76
Cool Hiphop Jabbawockeez Masquerade Mask Cosplay Costume Party Mask, White | Walmart | NA | 1 | 1 | https://www.walmart.com/ip/Cool-Hiphop-Jabbawockeez-Masquerade-Mask-Cosplay-Costume-Party-Mask-White/443043033 | 7.63 | 7.63
Thick Blank Male The Phantom Mask Costume White Face Mask Paintable | Walmart | 95430 | 1 | 6 | https://www.walmart.com/ip/Thick-Blank-Male-The-Phantom-Mask-Costume-White-Face-Mask-Paintable/956702597?selected=true | 17.82 | 17.82
Hitech RCD 36485 D-485Hw Karbonite Gear Ball Bearing Servo .15Sec/103oz @7.4V | Amazon | NA | 3 | 1 | https://www.amazon.com/Hitec-RCD-D485HW-Carbonite-Voltage/dp/B071YPPQ2V?s=hi | 25.49 | 76.47
ANYCUBIC 3D Printer Resin, 405nm SLA UV-Curing Resin with High Precision and Quick Curing & Excellent Fluidity for LCD 3D Printing - 1KG/Black | Amazon | NA | 1 | kg | https://www.amazon.com/dp/B07G35CC1V | 39.99 | 39.99
25ft - 1.5 inch PET Expandable Braided Sleeving – Black – Alex Tech braided cable sleeve | Amazon | N/A | 1 | 1 | ="https://www.amazon.com/25ft-Expandable-Braided-Sleeving-Sleeve/dp/B075QD7RP6" | 12.99 | 12.99
Wirefy 200 PCS Heat Shrink Tubing Kit - Larger Diameter - 3:1 Dual Wall Tube - Adhesive Lined - Marine Shrink Tubing - Black, Red | Amazon | NA | 1 | 200 | ="https://www.amazon.com/Wirefy-200-Heat-Shrink-Tubing/dp/B089D82FLG" | 13.99 | 13.99
ACTOO JST SM 3 Pin Connector LED Power Male to Female SM Wire Cable Adapter for WS2812B WS2812 WS2811 LED Light Strip 10 Pair | Amazon | NA | 2 | 10 | https://www.amazon.com/ACTOO-Connector-Female-Adapter-WS2812B/dp/B07GGPQXFC | 7.99 | 15.98
Xbox One Controller | Walmart | NA | 2 | 1 | ="https://www.microsoft.com/en-us/p/xbox-wireless-controller-arctic-camo-special-edition/9318snng3c5r?atc=true&cid=msft_web_collection" | 59.99 | 119.98
MR106-ZZ Bearing 6 x 10 x 3mm Both Sides Metal Shielded Ball Bearing Pre-Lubricated with Grease MR106-ZZ Radial Ball Bearing (10 Pack) | Amazon | NA | 2 | 10 | https://www.amazon.com/MR106-ZZ-Bearing-Shielded-Pre-Lubricated-Grease/dp/B08M9QN999 | 7.99 | 15.98
Fantasy Color Pale Flesh 400 mL Spray Can | Amazon | NA | 1 | 1 | https://www.amazon.com/Fantasy-Color-Pale-Flesh-Spray/dp/B07MFH9324 | 11.59 | 11.59
Amazon 5ft USB to Micro-USB Cable (designed for use with Fire tablets and Kindle E-readers) | Amazon | NA | 2 | 1 | ="https://www.amazon.com/Amazon-Micro-USB-designed-tablets-readers/dp/B0741WGQ36" | 9.99 | 19.98
Adafruit 9-DOF Absolute Orientation IMU Fusion Breakout - BNO055 | Adafruit | BNO055 | 3 | 1 | https://www.adafruit.com/product/2472 | 34.95 | 104.85
Quarton Red Dot Tiny Laser Module VLM-650-21 LPA (Mini-Size: Dimensions- D4 x 15 mm, Plastic Lens) | Amazon | NA | 6 | 1 | ="https://www.amazon.com/dp/B01KUSUBIM" | 30 | 180
HiLetgo 3pcs 650nm 5mw Laser Head Laser Tube Adjustable Focus 3~5V Red Laser Tube for Sight Positioning Sighting Telescope(Dot/Horizontal Line/Cross Optional) (Cross) | Amazon | NA | 2 | 3 | ="https://www.amazon.com/HiLetgo-Adjustable-Positioning-Telescope-Horizontal/dp/B072XDD3G4" | 8.49 | 16.98
PartyHop - Albert Einstein Mask - Halloween Realistic Famous People Celebrity Human Mask Brown | Amazon | NA | 1 | 1 | https://www.amazon.com/PartyCostume-Einstein-Halloween-Realistic-Celebrity/dp/B07H68S9BN | 16.99 | 16.99
Realistic Human Latex Mask Head Halloween Masquerade Novelty Masks Costume Dress | Amazon | NA | 1 | 1 | https://www.amazon.com/Realistic-Halloween-Masquerade-Novelty-Costume/dp/B0895DRXVD | 12.99 | 12.99
Qibaok Crimping Tool Kit Ratcheting Crimper with 1550PCS 2.54mm Dupont Connectors and 760pcs 2.54mm JST-XH Connectors for AWG 26-20(0.1-0.5mm²) | Amazon | N/A | 1 | 1 | https://www.amazon.com/Qibaok-Crimping-Ratcheting-Connectors-0-1-0-5mm%25C2%25B2/dp/B07ZK5F8HP | 39.99 | 39.99
Nextion Display 7" NX8048T070 Resistive Touch Screen UART HMI LCD Module 800x480 for Arduino Raspberry Pi | Amazon | NA | 1 | 1 | https://www.amazon.com/Nextion-NX8048T070-Display-Arduino-Raspberry/dp/B07QWPNW91 | 89.76 | 89.76
DEPEPE 30 Pcs 40 Pin 2.54mm Male and Female Pin Headers for Arduino Prototype Shield | Amazon | NA | 3 | 30 | ="https://www.amazon.com/DEPEPE-2-54mm-Headers-Arduino-Prototype/dp/B074HVBTZ4" | 5.49 | 16.47
KANGWEI 50 Pieces 2 Pin 5 mm Pinch PCB Mount Screw Terminal Block Connector 300V 10A (Green) | Amazon | NA | 3 | 50 | https://www.amazon.com/Pieces-Pinch-Mount-Terminal-Connector/dp/B01MT4LC0F | 7.65 | 22.95
Hitech RCD 36485 D-485Hw Karbonite Gear Ball Bearing Servo .15Sec/103oz @7.4V | Amazon | NA | 8 | 1 | https://www.amazon.com/Hitec-RCD-D485HW-Carbonite-Voltage/dp/B071YPPQ2V?s=hi | 25.49 | 203.92
DC Buck Converter, DROK DC to DC Step Down Power Supply Module 10V-65V to 0-60V 0-12A Adjustable Voltage Regulator Transformer Board with LED Display for Volt Reducer | Amazon | NA | 2 | 1 | ="https://www.amazon.com/dp/B08LPVWX74" | 29.99 | 59.98
ACR CAST RED 2423 PM .118 x 48 x 96 | Laird Plastics | ACR 2423 | 2 | 1 |  | 147.94 | 295.88
Realistic Human Latex Mask Head Halloween Masquerade Novelty Masks Costume Dress | Amazon | NA | 1 | 1 | https://www.amazon.com/Realistic-Halloween-Masquerade-Novelty-Costume/dp/B0895DRXVD | 12.99 | 12.99
PartyHop - Albert Einstein Mask - Halloween Realistic Famous People Celebrity Human Mask Brown | Amazon | NA | 1 | 1 | https://www.amazon.com/PartyCostume-Einstein-Halloween-Realistic-Celebrity/dp/B07H68S9BN | 16.99 | 16.99
Screw-on Bench-Mount Flat-Panel Monitor Ball-Grip Positioning Arm | McMaster-Carr | 5031T133 | 1 | 1 | https://www.mcmaster.com/5031T133/ | 125.63 | 125.63
Nextion Display 7" NX8048T070 Resistive Touch Screen UART HMI LCD Module 800x480 for Arduino Raspberry Pi | Amazon | NA | 1 | 1 | https://www.amazon.com/Nextion-NX8048T070-Display-Arduino-Raspberry/dp/B07QWPNW91 | 89.76 | 89.76
Makerfire Nextion HMI 2.4" TFT 320x240 Resistive Lcd Touch Screen Intelligent Display Module for Arduino NX3224T024 4M Flash, 2KByte RAM, 65k Colors | Amazon | NA | 2 | 1 | https://www.amazon.com/Makerfire-Nextion-Resistive-Intelligent-NX3224T024/dp/B013E3QCFQ | 24.98 | 49.96
Elegoo EL-CP-004 120pcs Multicolored Dupont Wire 40pin Male to Female, 40pin Male to Male, 40pin Female to Female Breadboard Jumper Wires Ribbon Cables Kit for arduino | Amazon | NA | 1 | 120 | ="https://www.amazon.com/Elegoo-EL-CP-004-Multicolored-Breadboard-arduino/dp/B01EV70C78" | 6.98 | 6.98
ACTOO JST SM 3 Pin Connector LED Power Male to Female SM Wire Cable Adapter for WS2812B WS2812 WS2811 LED Light Strip 10 Pair | Amazon | NA | 1 | 10 | https://www.amazon.com/ACTOO-Connector-Female-Adapter-WS2812B/dp/B07GGPQXFC | 7.99 | 7.99
ELEGOO UNO R3 2.8 Inches TFT Touch Screen with SD Card Socket w/All Technical Data in CD for Arduino UNO R3 | Amazon | NA | 1 | 1 | https://www.amazon.com/Elegoo-EL-SM-004-Inches-Technical-Arduino/dp/B01EUVJYME | 16.99 | 16.99
KeeYees 5M GT2 Timing Belt 6mm Width + 4pcs 20 Teeth 5mm Bore Belt Pulley Wheel + 4pcs Idler + 4pcs Tensioner Spring Torsion + 2pcs Gear Clamp Mount Block with Allen Wrench for 3D Printer RepRap | Amazon | NA | 1 | 1 | https://www.amazon.com/KeeYees-Timing-Tensioner-Torsion-Printer/dp/B07JKT5BZQ | 15.99 | 15.99
Needle-Roller Thrust Bearing for 8 mm Shaft Diameter, 21 mm OD | McMaster-Carr | 5909K3 | 4 | 1 | https://www.mcmaster.com/5909K3/ | 5.31 | 21.24
1 mm Thick Washer for 8 mm Shaft Diameter Needle-Roller Thrust Bearing | McMaster-Carr | 5909K295 | 8 | 1 | https://www.mcmaster.com/5909K295/ | 1.58 | 12.64
uxcell M3 x 250mm Fully Threaded Rod, 304 Stainless Steel, Right Hand Threads | Amazon | NA | 1 | 1 | ="https://www.amazon.com/uxcell-250mm-Threaded-Stainless-Threads/dp/B078H58XVL" | 8.49 | 8.49
Awclub 2pcs M2 x 250mm Fully Threaded Rod, 304 Stainless Steel Long Threaded Screw,Right Hand Threads for Anchor Bolts,Clamps,Hangers and U-Bolts | Amazon | NA | 1 | 1 | ="https://www.amazon.com/Awclub-Threaded-Stainless-Threads-Hangers/dp/B08952HPYL" | 7.49 | 7.49
HELIFOUNER 210 Pieces 7 Sizes 304 Stainless Steel Lock Nut Assortment Kit (M3 M4 M5 M6 M8 M10 M12) | Amazon | NA | 1 | 210 | https://www.amazon.com/HELIFOUNER-Pieces-Sizes-Stainless-Assortment/dp/B08CHK82N2 | 11.99 | 11.99
MR106-ZZ Bearing 6 x 10 x 3mm Both Sides Metal Shielded Ball Bearing Pre-Lubricated with Grease MR106-ZZ Radial Ball Bearing (10 Pack) | Amazon | NA | 1 | 10 | https://www.amazon.com/MR106-ZZ-Bearing-Shielded-Pre-Lubricated-Grease/dp/B08M9QN999 | 7.99 | 7.99
DC Buck Converter, DROK DC to DC Step Down Power Supply Module 10V-65V to 0-60V 0-12A Adjustable Voltage Regulator Transformer Board with LED Display for Volt Reducer | Amazon | NA | 1 | 1 | ="https://www.amazon.com/dp/B08LPVWX74" | 29.99 | 29.99
Hitech RCD 36485 D-485Hw Karbonite Gear Ball Bearing Servo .15Sec/103oz @7.4V | Amazon | NA | 4 | 1 | https://www.amazon.com/Hitec-RCD-D485HW-Carbonite-Voltage/dp/B071YPPQ2V?s=hi | 25.49 | 101.96
ELEGOO UNO R3 2.8 Inches TFT Touch Screen with SD Card Socket w/All Technical Data in CD for Arduino UNO R3 | Amazon | NA | 1 | 1 | https://www.amazon.com/Elegoo-EL-SM-004-Inches-Technical-Arduino/dp/B01EUVJYME | 16.99 | 16.99
Green Laser Module Diode Green Laser Beam Light 532nm (5mw Green Dot) | Amazon | NA | 3 | 1 | https://www.amazon.com/dp/B07L4PZKF4/ref=twister_B07L4QCJ9C?_encoding=UTF8&psc=1 | 16.98 | 50.94
Fairfield Project Foam Multi-Purpose Foam, 24" x 72" x 1", 1 Each | Walmart | 552875504 | 1 | 1 | https://www.walmart.com/ip/Fairfield-Project-Foam-Multi-Purpose-Foam-24-x-72-x-1-1-Each/41386701 | 15.97 | 15.97
SainSmart USB Host Android ADK Shield 2.0 For Arduino Uno Mega R3 Mega 2560 Duemilanove Nano Robot | SainSmart | 101-50-131 | 2 | 1 | https://www.sainsmart.com/products/sainsmart-usb-host-android-adk-shield-2-0-for-arduino-uno-mega-r3-mega2560-duemilanove-nano-robot?currency=USD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 | 17.99 | 35.98
Duck Brand 12 in. x 150 ft. Clear Original Bubble Wrap Cushioning | Walmart | 286677 | 1 | 1 | https://www.walmart.com/ip/Duck-Brand-24-inches-x-35-feet-Clear-Original-Bubble-Wrap/50314466 | 16.88 | 16.88
M2 M3 M4 Alloy Steel Screws Nuts and Washers 1200PCS, Sutemribor Hex Socket Head Cap Bolts Screws Nuts Washers Assortment Kit with Hex Wrenches | Amazon | NA | 1 | 1200 | https://www.amazon.com/Washers-1200PCS-Sutemribor-Assortment-Wrenches/dp/B07H4MG7TC | 26.99 | 26.99
Reflective Floor Marking Tape 1" Wide, 15 Feet Long | McMaster-Carr | 5997T81 | 1 | 1 | https://www.mcmaster.com/5997T81/ | 6.92 | 6.92
HiLetgo 3pcs GY-521 MPU-6050 MPU6050 3 Axis Accelerometer Gyroscope Module 6 DOF 6-axis Accelerometer Gyroscope Sensor Module 16 Bit AD Converter Data Output IIC I2C for Arduino | Amazon | NA | 1 | 3 | https://www.amazon.com/HiLetgo-MPU-6050-Accelerometer-Gyroscope-Converter/dp/B00LP25V1A?th=1 | 8.99 | 8.99
Xbox One Controller | Walmart | NA | 1 | 1 | ="https://www.microsoft.com/en-us/p/xbox-wireless-controller-arctic-camo-special-edition/9318snng3c5r?atc=true&cid=msft_web_collection" | 59.99 | 59.99
HS-422 Servo-Clockwise (stock)-Stock Rotation | Servocity | HS-422 | 4 | 1 | https://www.servocity.com/hs-422-servo/ | 14.49 | 57.96
Arduino Mega | Amazon | NA | 2 | 1 | ="https://www.amazon.com/ELEGOO-ATmega2560-ATMEGA16U2-Projects-Compliant/dp/B01H4ZLZLQ" | 16.86 | 33.72
HS-422 Servo-Clockwise (stock)-Stock Rotation | Servocity | HS-422 | 4 | 1 | https://www.servocity.com/hs-422-servo/ | 14.49 | 57.96
ACR CAST RED 2423 PM .118 x 48 x 96 | Laird Plastics | ACR 2423 | 1 | 1 |  | 147.94 | 147.94
Anker 4-Port USB 3.0 Hub, Ultra-Slim Data USB Hub with 2 ft Extended Cable [Charging Not Supported], for MacBook, Mac Pro, Mac mini, iMac, Surface Pro, XPS, PC, Flash Drive, Mobile HDD | Amazon | NA | 1 | 1 | https://www.amazon.com/Anker-Extended-MacBook-Surface-Notebook/dp/B07L32B9C2 | 12.99 | 12.99
6ft USB 3.0 A Male to A Male Cable Cord Lead Black Blue | Amazon | NA | 1 | 1 |  | 7.42 | 7.42
Microsoft Xbox Wireless Controller + Wireless Adapter for Windows 10 - Xbox | Microsoft | NA | 1 | 1 |  | 74.99 | 74.99
10ft Charger Cable for PS5 DualSense and Xbox Series X|S Controller, YUANHOT Nylon Braided USB Type C Fast Charging Cord with LED for PlayStation 5, Xbox Series X, Switch Pro Controller and More | Walmart | NA | 1 | 1 | https://www.walmart.com/ip/10ft-Charger-Cable-PS5-DualSense-Xbox-Series-X-S-Controller-YUANHOT-Nylon-Braided-USB-Type-C-Fast-Charging-Cord-LED-PlayStation-5-X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 | 13.99 | 13.99
Xbox Wireless Controller – Robot White | Walmart | NA | 1 | 1 | https://www.walmart.com/ip/Xbox-Wireless-Controller-Robot-White/897028435 | 49.99 | 49.99
Electop 2 Pack USB 2.0 A Female to USB B Print Male Adapter Converte | Amazon | 5320743 | 1 | 2 | https://www.amazon.com/Electop-Female-Print-Adapter-Converter/dp/B014RESWU4 | 8.69 | 8.69
Thick Blank Male The Phantom Mask Costume White Face Mask Paintable | Walmart | 95430 | 1 | 6 | https://www.walmart.com/ip/Thick-Blank-Male-The-Phantom-Mask-Costume-White-Face-Mask-Paintable/956702597?selected=true | 17.82 | 17.82
25ft - 1/4 inch PET Expandable Braided Sleeving – Black – Alex Tech Braided Cable Sleeve | Amazon | N/A | 1 | 25ft | https://www.amazon.com/gp/product/B071JH14WZ/ref=ox_sc_act_title_1?psc=1&smid=A2N7NRZ9X3BHHN | 7.5 | 7.5
ACR CAST RED 2423 PM .118 x 48 x 96 | Laird Plastics | ACR 2423 | 1 | 1 |  | 147.94 | 147.94
Kable Kontrol® Nylon Braided Cable Sleeving | CTA Cable Ties and More | BSLNY050 | 20 | 1 | https://www.cabletiesandmore.com/nylon-braided-sleeving?pid=3880 | 0.64 | 12.8
Black Plastic Drag Chain Cable Carrier 10 x 15mm for CNC Router Mill | Amazon | A11110200ux0144 | 1 | 1 | ="https://www.amazon.com/Black-Plastic-Chain-Carrier-Router/dp/B00880AVL2?hvadid=198071192844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" | 9.99 | 9.99
3Dman 15A 250V Rocker Switch Power Socket Inlet Module Plug 5A Fuse Switch with 18 AWG Wiring 3 Pin IEC320 C14-2pcs | Amazon | B07RQV2NPN | 1 | 1 | https://www.amazon.com/3Dman-Rocker-Switch-Socket-C14-2pcs/dp/B07RQV2NPN | 11.99 | 11.99
C2G Power Cord, Universal Power Cord, 14 AWG, Black, 6 Feet (1.82 Meters), Cables to Go 03131 | Amazon | B00009OLLS | 1 | 1 | ="https://www.amazon.com/dp/B00009OLLS" | 6.54 | 6.54
Ocular Imaging Eye Model | Ocular Instruments | OEMI-7 | 2 | 1 | https://ocularinc.com/products/educational-aides/ocular-imaging-eye-model.html | 625 | 1250
Fashion Cosplay Mask for Halloween Masquerade Party | Amazon | B07CKF2R8Z | 5 | 1 | https://www.amazon.com/Jabbawockeez-Hip-hop-Halloween-Cosplay-Costume/dp/B013ULOYU2 | 8.79 | 43.95
Screw-on Bench-Mount Flat-Panel Monitor Ball-Grip Positioning Arm | McMaster-Carr | 5031T133 | 1 | 1 | https://www.mcmaster.com/5031T133/ | 125.63 | 125.63
GE 6 Outlet Surge Protector, 10 Ft Extension Cord, Power Strip, 800 Joules, Flat Plug, Twist-to-Close Safety Covers, White, 14092 | Amazon | NA | 1 | 1 | https://www.amazon.com/GE-Outlet-Protector-Extension-14092/dp/B00DOMYL24?s=electronics | 18.99 | 18.99
ALPEC KEYCHAIN RED LASER POINTER 4241 | Wiringdepot | NA | 3 | 1 | https://www.wiringdepot.com/alpec-keychain-red-laser-pointer-4241.aspx | 11.95 | 35.85
NTE Electronics 25-B500-10 Series 25-B500 Terminal Block Barrier Strip, Dual Row Panel Mount, 20 Amp, Dual Row, 10 Pole, 9.50 mm Pitch, 300V, 22-14 AWG Wire Range | Amazon | B0084LH4ZG | 2 | 1 | https://www.amazon.com/NTE-Electronics-25-B500-10-25-B500-Terminal/dp/B0084LH4ZG?s=industrial | 6.38 | 12.76
R REIFENG 6 Pack Mechanical Endstop Limit Switch Module Endstop Switch Horizontal Type with 1M Cable for 3D Print Parts Ramps1.4 | Amazon | B07PCN6T6F | 1 | 6 | ="https://www.amazon.com/dp/B07PCN6T6F" | 9.49 | 9.49
Button Head Hex Drive Screw Black-Oxide Alloy Steel, 1/4"-20 Thread, 1/2" Long | McMaster-Carr | 91255A537 | 4 | 50 | https://www.mcmaster.com/91255A537/ | 7.08 | 28.32
Silver Corner Bracket, 1" Long for 1" High Rail T-Slotted Framing | McMaster-Carr | 47065T236 | 42 | 1/EA | https://www.mcmaster.com/47065T236/ | 5.21 | 218.82
T-Slotted Framing End-Feed Single Nut, 1/4"-20 Thread | McMaster-Carr | 47065T905 | 5 | 25 | https://www.mcmaster.com/47065T905/ | 5.44 | 27.2
T-Slotted Framing Single Rail, Silver, 1" High x 1" Wide, Solid | McMaster-Carr | 47065T101 | 3 | 6 ft | https://www.mcmaster.com/47065T101-47065T122/ | 17.68 | 53.04
Wathai DC Brushless Cooling Fan 80mm 80x25mm 24V Heatsink Cooler Radiator Fans | Amazon | N/A | 1 | 1 | https://www.amazon.com/Wathai-Brushless-Cooling-Heatsink-Radiator/dp/B07PFP7L4F?s=electronics | 8.99 | 8.99
Multipurpose 6061 Aluminum 90 Degree Angle, 4ft | McMaster-Carr | 8982K17 | 1 | 1 | https://www.mcmaster.com/8982K17/ | 25.18 | 25.18
400mm linear rail | Amazon | NA | 1 | 1 | https://www.amazon.com/Twotrees-Sliding-Guideway-Bearing-Printer/dp/B07SL1HHSS | 23.99 | 23.99
Noctua NF-A8 PWM, Premium Quiet Fan, 4-Pin (80mm, Brown) | Amazon | N/A | 1 | 1 | ="https://www.amazon.com/Noctua-NF-A8-PWM-Premium-Quiet/dp/B00NEMG62M" | 15.95 | 15.95
WINSINN 80mm Fan 24V Brushless 8025 80x25mm for Cooling PC Computer Case CPU Set-top Box Router Receiver DVR Playstation Xbox - High Speed (Pack of 2Pcs) | Amazon | B07H76Z5Y2 | 1 | 2 | https://www.amazon.com/WINSINN-Brushless-Computer-Receiver-Playstation/dp/B07H76Z5Y2 | 10.98 | 10.98
Noctua NF-P12 redux-900, Ultra Quiet Silent Fan, 3-Pin, 900 RPM (120mm, Grey) | Amazon | N/A | 1 | 1 | ="https://www.amazon.com/Noctua-redux-900-Ultra-Quiet-Award-Winning-Affordable/dp/B07C5KZX85" | 13.9 | 13.9
Haisstronica Solder Seal Wire Connectors, Heat Shrink Solder Connectors Insulated Marine Automotive Terminals with Case（50Red 22-18） | Amazon | N/A | 1 | 50pcs | https://www.amazon.com/dp/B07C3MKM3K/ref=cm_sw_r_cp_apa_fabc_YE63Z5P7K72E6FDPZ5TW | 9.99 | 9.99
BNTECHGO 20 Gauge Silicone Wire Kit Red Black White Blue and Green Each 30ft 20 AWG Stranded Wire | Amazon | N/A | 1 | 30ft x5 | https://www.amazon.com/gp/product/B06Y5L4T86/ref=ox_sc_act_title_1?psc=1&smid=AITZO53LNBA1K | 14.98 | 14.98
TOUHIA 2.54mm Pitch 4-Pin PCB Mount Screw Terminal Block Connector for Arduino, Rated 150V 6A - Pack of 20 | Amazon | N/A | 1 | 20 Pack | https://www.amazon.com/gp/product/B07PN8XSMC/ref=ox_sc_act_title_2?psc=1&smid=A39QRGD6IK86BO | 8.99 | 8.99
TUOFENG 4 Colors Lights Line 40 ft Spools RGB Extension Cable Line 4 pin 20 AWG Electrical Wire for Single LED Strip Light | Amazon | N/A | 1 | 40ft | https://www.amazon.com/gp/product/B0793MSGYZ/ref=ox_sc_act_title_3?psc=1&smid=A1P2Y1BEUUWGO2 | 14.99 | 14.99
Striveday 22 AWG 3 conductor wire Power Cable Audio Cable Signal Line (Red & Black & yellow) 33ft UL certification | Amazon | N/A | 1 | 33ft | https://www.amazon.com/gp/product/B07Y34GL7K/ref=ox_sc_act_title_4?psc=1&smid=ANPVYBWUHNHQ2 | 14.99 | 14.99
Qunqi 400 tie Point Experiment Mini Breadboard 5.5×8.2×0.85cm | Amazon | MK-003 | 1 | 1 | https://www.amazon.com/Qunqi-point-Experiment-Breadboard-5-5%25C3%25978-2%25C3%25970-85cm/dp/B0135IQ0ZC | 4.99 | 4.99
LM YN 1-Channel Relay Module High Low Level Trigger Optocoupler Isolation With Indicator light for Arduino (5V) | Amazon | B077PS7767 | 1 | 1 | ="https://www.amazon.com/LM-YN-Triggering-Optocoupler-Applications/dp/B077PS7767?hvadid=242027088707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" | 5.99 | 5.99
inShareplus 24V 16.5A 400W Universal Regulated Switching Power Supply, 100-240V AC to DC 24 Volt LED Driver, Converter, Transformer, Adapter for LED Strip Light, CCTV, Computer Project, 3D Printer | Amazon | ISP-KGDY-24V-400W | 1 | 1 | ="https://www.amazon.com/dp/B07RHJ53C9" | 25.99 | 25.99
Silver Corner Bracket, 1" Long for 1" High Rail T-Slotted Framing | McMaster-Carr | 47065T236 | 20 |  | https://www.mcmaster.com/47065T236/ | 5.21 | 104.2
T-Slotted Framing Silver 90 Degree Angle Bracket for 1" High Rail, 4" Long | McMaster-Carr | 3136N148 | 4 | 1 | https://www.mcmaster.com/3136N148/ | 13.83 | 55.32
T-Slotted Framing End-Feed Single Nut, 1/4"-20 Thread | McMaster-Carr | 47065T905 | 2 | 25 | https://www.mcmaster.com/47065T905/ | 5.44 | 10.88
400mm Travel Length Linear Stage Actuator DIY CNC Router Parts X Y Z Linear Rail | Amazon | CBX1605-400A | 2 |  | ="https://www.amazon.com/Actuator-CBX1605-Ballscrew-Motorized-Stepper/dp/B078CYDBST" | 109.8 | 219.6
300mm Travel Length Linear Rail Guide Ballscrew Sfu1605 DIY CNC Router Parts X Y Z Linear Stage Actuator with NEMA17 Stepper Motor | Amazon | CBX1605-300A | 1 |  | ="https://www.amazon.com/Actuator-CBX1605-Ballscrew-Motorized-Stepper/dp/B077XX4TPL" | 107 | 107
T-Slotted Framing Single Rail, Silver, 1" High x 1" Wide, Solid | McMaster-Carr | 47065T101 | 5 | 6 ft | https://www.mcmaster.com/47065T101-47065T122/ | 17.68 | 88.4
TB6600 Stepper Driver | Amazon | TB6600 | 3 | 1 | ="https://www.amazon.com/UsongShine-Stepper-Controller-Arduino-Printer/dp/B07HHS14VQ" | 11.99 | 35.97
SainSmart USB Host Android ADK Shield 2.0 For Arduino Uno Mega R3 Mega 2560 Duemilanove Nano Robot | SainSmart | 101-50-131 | 1 | 1 | https://www.sainsmart.com/products/sainsmart-usb-host-android-adk-shield-2-0-for-arduino-uno-mega-r3-mega2560-duemilanove-nano-robot?currency=USD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 | 17.99 | 17.99
Usongshine MGN12C Linear Bearing Sliding Block Match | Amazon | NA | 1 | 1 | ="https://www.amazon.com/Usongshine-Bearing-Sliding-Engraving-Machine/dp/B088DB8FY6" | 25.98 | 25.98
UEETEK 4 Pcs 1M Stepper Motor Cables Lead Wire HX2.54 4 pin to 6 pin | Amazon | B073VKPD1Q | 2 | 1 | Amazon.com:%2520UEETEK%25204%2520Pcs%25201M%2520Stepper%2520Motor%2520Cables%2520Lead%2520Wire%2520HX2.54%25204%2520pin%2520to%25206%2520pin:%2520Industrial%2520&%2520Scientific | 10.39 | 20.78
6063 Aluminum U Channel | Amazon | NA | 2 | 1 | https://www.amazon.com/Aluminum-U-Channel-Unpolished-Extruded-Thickness/dp/B003U6IANA?s=industrial | 22.08 | 44.16
USB Connectors USBA-USB B A Adapter Fdthru Black | Mouser Electronics | NAUSB-W-B | 2 | 1/EA | https://www.mouser.com/ProductDetail/Neutrik/NAUSB-W-B | 6.39 | 12.78
12pcs Adjustable Pushrod Connector Linkage Stopper+12pcs Steel Z Push Rods+2pcs Hex Wrench | Amazon | NA | 1 | 12 | ="https://www.amazon.com/dp/B0839C2BRV" | 10.89 | 10.89
HS-422 Servo-Clockwise (stock)-Stock Rotation | Servocity | HS-422 | 4 | 1 | https://www.servocity.com/hs-422-servo/ | 14.49 | 57.96
Arduino Mega | Amazon | NA | 1 | 1 | ="https://www.amazon.com/ELEGOO-ATmega2560-ATMEGA16U2-Projects-Compliant/dp/B01H4ZLZLQ" | 16.86 | 16.86
24V DC Power Supply | Amazon | NA | 1 | 1 | https://www.amazon.com/MEAN-WELL-LRS-350-24-Switching-Printer/dp/B07SQLJG5L?s=industrial | 44 | 44
BEA Electrosales - LASER-650-5D | wolfautomation | LASER-650-5D | 2 | 1 | https://www.wolfautomation.com/class-1-laser-laser-pointer-3-5vdc-650nm-1/ | 31.9 | 63.8
 |  |  |  |  |  |  |  | Total | 6005.25

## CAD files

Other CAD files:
CAD/Combined CAD files/Assembly FINAL.SLDASM
CAD/Combined CAD files/Assembly Rail 300mm [MK2].SLDASM
CAD/Combined CAD files/Assembly Gantry [MK2].SLDASM
CAD/Combined CAD files/Assembly Rail 400mm [MK2].SLDASM
CAD/Combined CAD files/Surface Assembly.SLDASM
CAD/Combined CAD files/LCD Screen Assembly.SLDASM
CAD/Combined CAD files/Assembly Aluminium Frame.SLDASM
CAD/Combined CAD files/Z-Bracket w Stepper.SLDASM
CAD/Combined CAD files/Assembly_Control_Box[MK2].SLDASM
CAD/Combined CAD files/Total Assembly.SLDASM
CAD/Combined CAD files/Eye Rig MK4.SLDASM
CAD/Combined CAD files/Base Rail 300mm.SLDPRT
CAD/MASCOT Wiring Diagram/WSU ME416 Wiring PCB FINAL.dwg
CAD/Combined CAD files/Motor Rail.SLDPRT
CAD/Combined CAD files/Holder Yaw Eye Laser [MK3].SLDPRT
CAD/Combined CAD files/Holder Roll Eye[MK3].SLDPRT
CAD/Combined CAD files/Corner Bottom[MK2].SLDPRT
CAD/Combined CAD files/Back Wall[MK2].SLDPRT
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

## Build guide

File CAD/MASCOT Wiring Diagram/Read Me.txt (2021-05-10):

Guide for wire ampacity: https://www.powerstream.com/Wire_Size.htm
	Use "Max Amps for Chassis Wiring"
	Consider that wiring in series (ex. TB6600s) wire carry more amps

Diagrams best used with AutoCAD 2018 or later

Kyle B.

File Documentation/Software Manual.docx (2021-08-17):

EYE TRACKER TESTING ROBOT

SOFTWARE INSTRUCTION MANUAL

Content:

- Pull GitHub files
- Flashing the EEPROM
- Flashing the Arduino Code
- Windows API

Pull GitHub files –

1. Open github.com/jpswensen/EyeTrackingTestRig *replace with MSResearch Github link* and clone the repository onto your local machine.
2. This repository contains the API, Arduino Code and the CAD files associated with the robot.

Flashing the EEPROM –

The Arduino code upon boot-up expects certain variables to be present in the EEPROM, in certain pre-defined addresses. The robot will not function as expected if these variables are not present or the wrong values for these variables are loaded. So, if this the first time that you will be flashing the Arduino, it is necessary to flash the EEPROM before. Below are the steps to follow to flash the EEPROM.

1. Navigate to Arduino CODE -> EyeTrackerRevamped -> EEPROMFlasher
2. Open EEPROMFlasher.ino. Select the COM port associated with the robot’s Arduino Mega.
3. Upload the code.

Now the required variables should be loaded onto the EEPROM.

Flashing the Arduino Code –

1. Navigate to Arduino CODE -> EyeTrackerRevamped.
2. Open EyeTrackerRevamped.ino and upload this file onto the Arduino Mega.
3. Once the file is done uploading, you should hear the relay in the electrical box make a clicking sound and the eye servos should rotate to their “home” position.

Once the Arduino has been flashed, you should be set to start controlling the robot.

Windows API –

In order for the API to work with the Arduino, you will need a USB to TTL Serial cable like the one in the link here: 954 Adafruit Industries LLC | Cable Assemblies | DigiKey (https://www.digikey.com/en/products/detail/adafruit-industries-llc/954/7064488)

The pin out for this cable should be as follows:

Red -> 5V on the Arduino; Black -> GND on the Arduino; White (RX) -> TX on the Arduino; Green (TX) -> TX on the Arduino.

Once the USB to TTL Serial Cable has been connected to the Arduino, connect it to the PC you are using for controlling the robot.

1. Navigate to EyeRobotControlApp -> EyeRobotControlApp -> bin -> Debug.
2. Open EyeRobotControlApp.exe.
3. Enter the COM port associated with the USB to Serial Cable in the window that pops up.

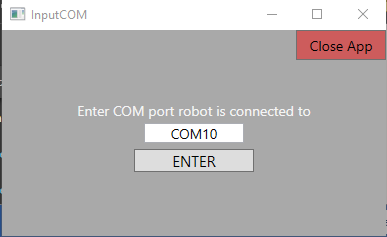
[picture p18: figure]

Figure 1 COM Port Window

4. If the COM port entered was right, you should see the screen given below.

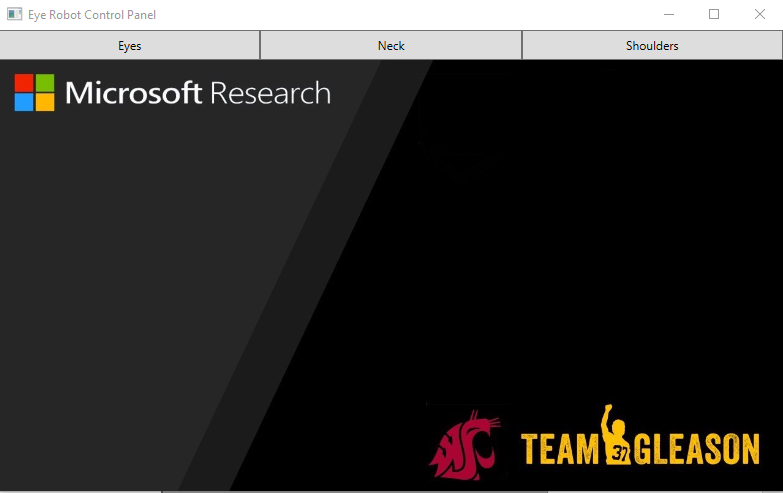
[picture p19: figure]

Figure 2 Robot Control Application Main Window

The Windows API has three tabs or pages: Eye Control, Neck Control and Shoulder Control. These three pages provide all the functionalities of the robot. Each page also has a corresponding calibration window that allows one to calibrate the associated subsystem.

Eye Control Page –

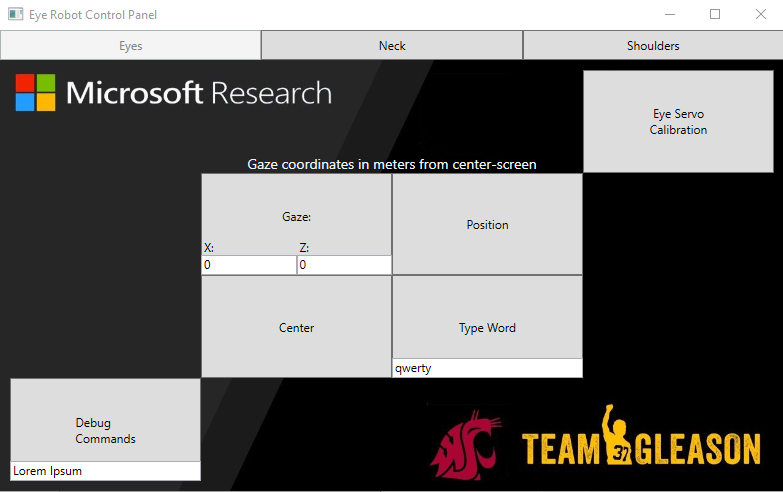
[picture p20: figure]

Figure 3 Eye Control Page

1. To point the eyes at a desired position on the screen, type out the coordinates in the text boxes under Gaze and click on the Gaze button to make the eyes point at that position. Note: the coordinates are in meters, so X and Y values greater than 0.1 will make the eyes point outside the screen.
2. Clicking on the center button will send the eyes to the center position on the screen.
3. To calibrate the eyes, click on the Eye Servo Calibration button and a window as given below should pop up.

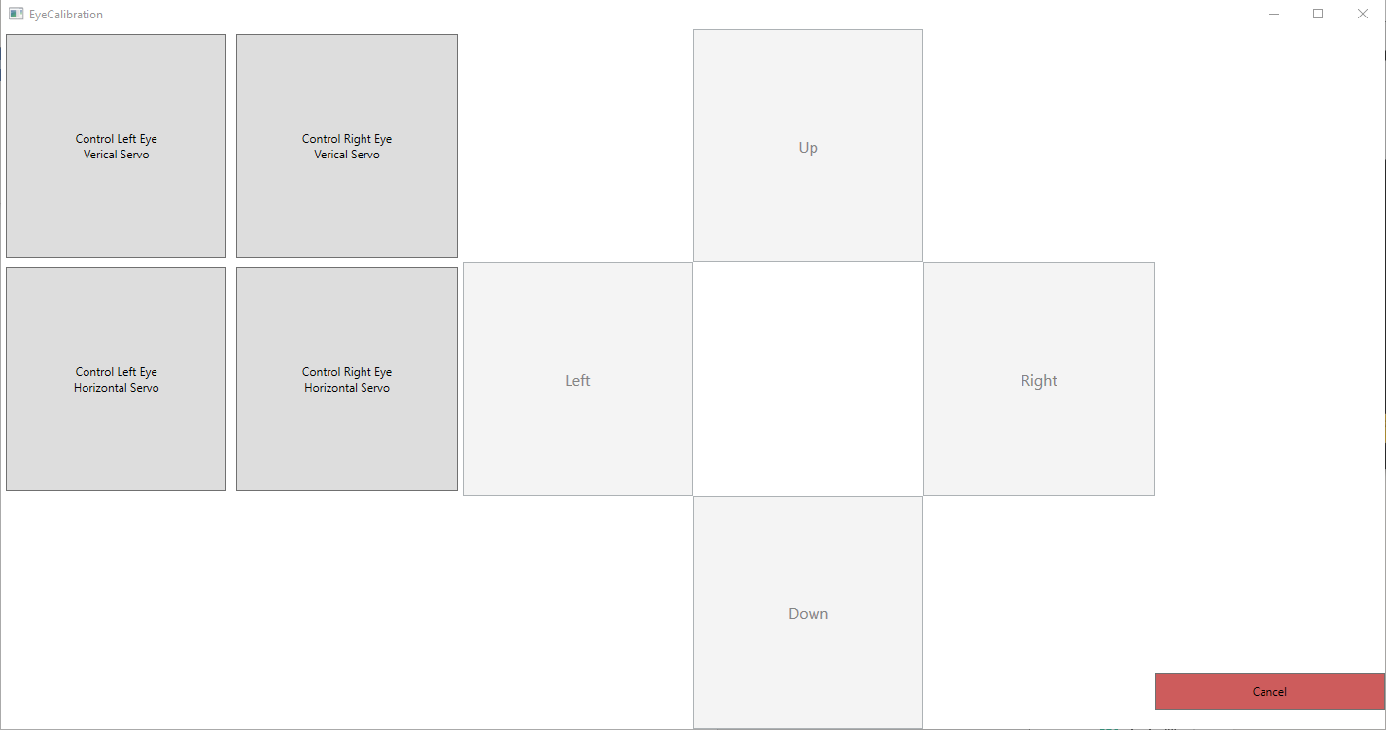
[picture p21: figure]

Figure 4 Eye Calibration Window

4. In this window, you can select which eye servo you wish to control and move that servo Up-Down or Left-Right.
5. Once you have managed to get both eyes to point at a single point at the center of the screen, you can exit the calibration process by pressing the CANCEL button.

Neck Control Page –

1. The neck control page allows the user to manually control the neck of the robot and direct it toward the desired angle. All angles are accepted in radians.
2. PhiR indicates the amplitude of the twist and PhiS indicates the direction of the twist (0⁰ is straight forward; 90⁰ is to the right; 180⁰ is to the left). PhiD indicates the angle of yaw of the neck.
3. To move the neck input the desired coordinates in their respective positions and press set.
4. To calibrate the neck, press the calibrate button and the calibration window as shown in figure 6 should pop up.

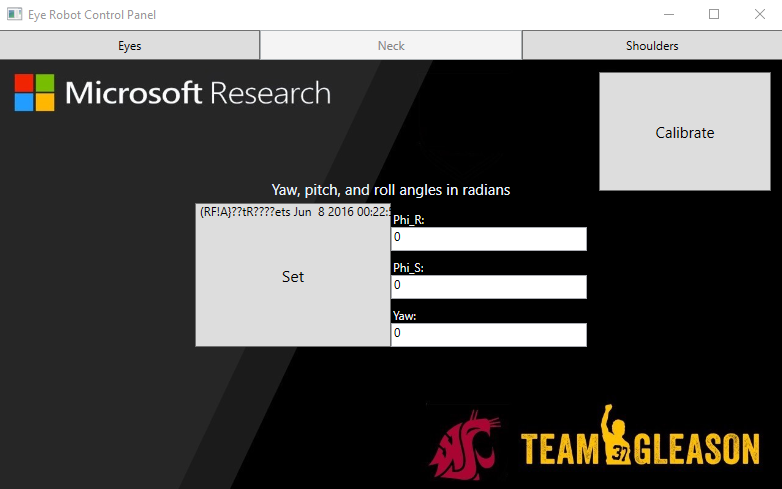
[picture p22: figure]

Figure 5 Neck Control Page

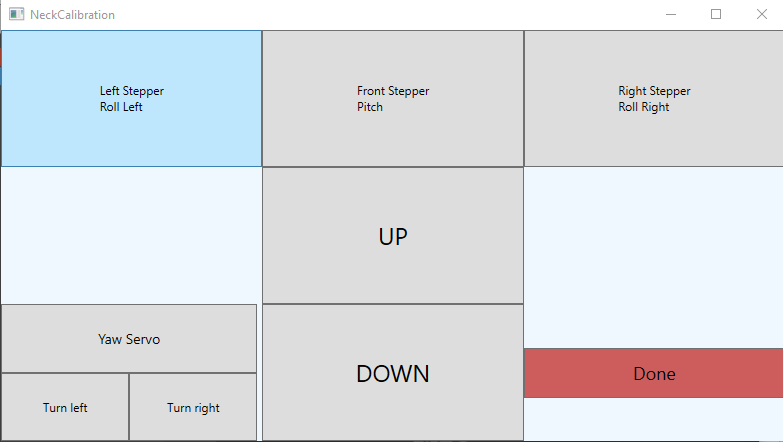
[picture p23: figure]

Figure 6 Neck Calibration Page

5. Select the desired motor to calibrate in the calibration page and up/down to loosen or tighten the respective neck stepper. Once finished calibrating, press the Done button to exit the window and save the set calibration variables to the PROM.

Shoulder Control Page –

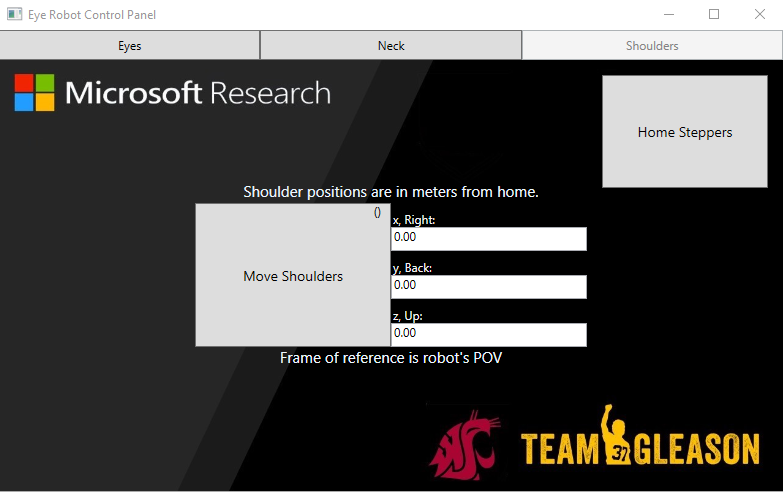
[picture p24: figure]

Figure 7 Shoulder Control Page

1. The shoulder control page allows for manual control of the shoulder of the robot.
2. Upon first-time bootup, always calibrate the shoulder by pressing the home steppers button. Doing so will move the shoulders to their zero or home position.
3. To move the shoulder to the desired coordinates, input the X,Y,Z coordinates in their respective text boxes and press move shoulders button.

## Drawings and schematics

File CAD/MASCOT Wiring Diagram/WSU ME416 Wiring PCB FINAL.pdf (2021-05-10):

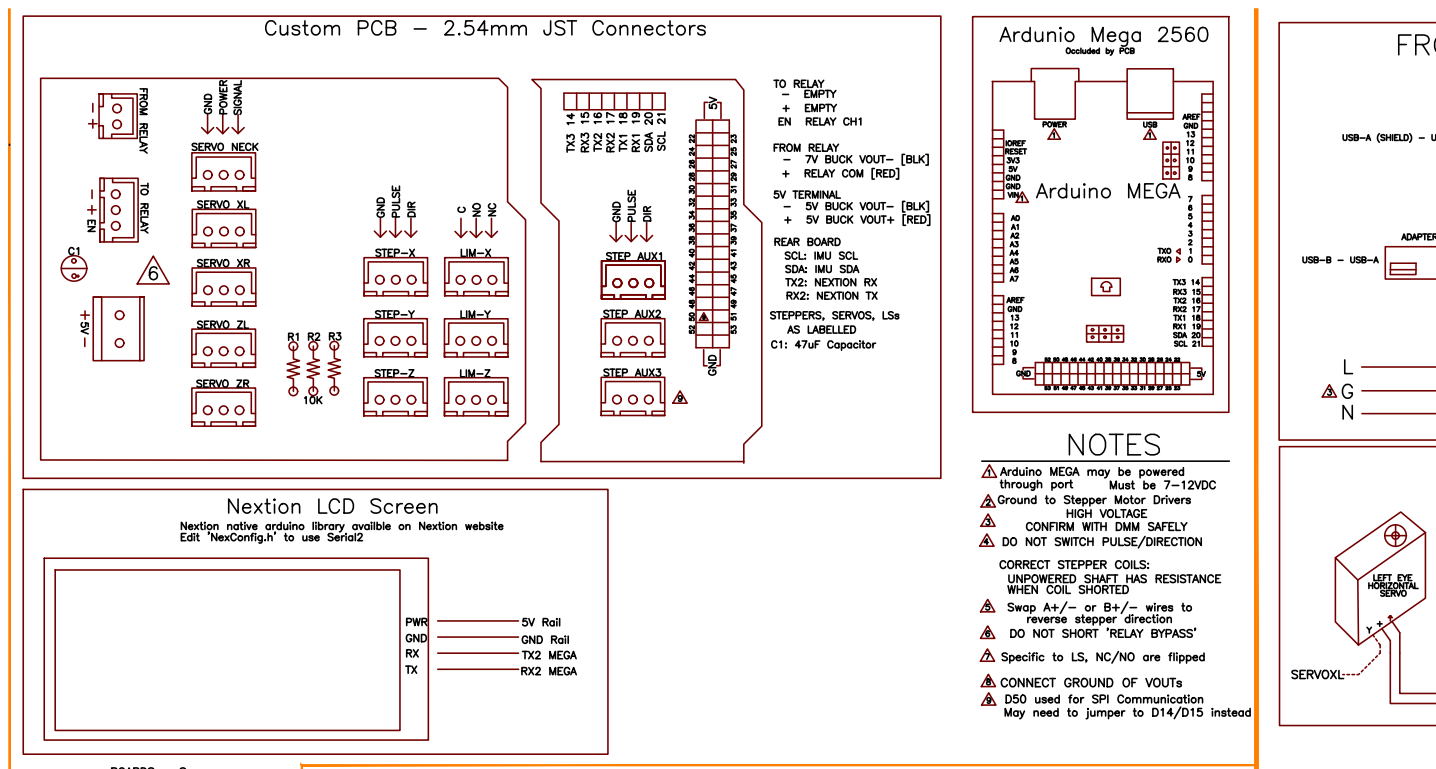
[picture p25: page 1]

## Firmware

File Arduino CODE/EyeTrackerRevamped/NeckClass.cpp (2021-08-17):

#include "NeckClass.h"

NeckMotor neckCalibrationMotor = front;

// Stepper Configuration variables.
float spoolRadius = 0.0071;                      // radius of the spool that holds the thread
float spoolCircumference = 2.0 * M_PI * spoolRadius; // circumference of the spool
float mmPerRevs = spoolCircumference;            // mm of thread that each revolution of spool will loosen or tighten
float stepsPerRev = 3838;                        // number of steps in one revolution for the neck steppers
float mmPerStep = mmPerRevs / stepsPerRev;       // mm of thread released in one step

// The known stepper pos after calibration. = (known cable length)/ mmPerStep
// 0.127 is the length of calibration stick and hence the known cable length.
float knownStepperPos = 0.127 / mmPerStep;

// number of microseconds per degree for yaw servo
float yawMicroSecondsPerDegree = 2000.00 / 270.00 * 2.4;

/*
   Neck Class constructor.
*/
RobotNeck::RobotNeck()
{
}

/*
   Neck Class destructor to clear pointer objects.
*/
RobotNeck::~RobotNeck()
{
  delete[] this->frontStepper;
  delete[] this->backLeftStepper;
  delete[] this->backRightStepper;
}

/*
   Function to initialize the Neck objects. Function also sets the maxspeed
   and acceleration for the stepper objects as well.
*/
void RobotNeck::init()
{
  this->frontStepper = new AccelStepper(AccelStepper::DRIVER, frontPulse, frontDir);
  this->backLeftStepper = new AccelStepper(AccelStepper::DRIVER, backLeftPulse, backLeftDir);
  this->backRightStepper = new AccelStepper(AccelStepper::DRIVER, backRightPulse, backRightDir);

  this->m3FrontStepper.init(frontDir, frontPulse);
  this->m3BackRightStepper.init(backRightDir, backRightPulse);
  this->m3BackLeftStepper.init(backLeftDir, backLeftPulse);

  this->m3FrontStepper.SetSpeed(1000);
  this->m3BackRightStepper.SetSpeed(1000);
  this->m3BackLeftStepper.SetSpeed(1000);

  this->m3FrontStepper.SetCurrentPosition(knownStepperPos);
  this->m3BackRightStepper.SetCurrentPosition(knownStepperPos);
  this->m3BackLeftStepper.SetCurrentPosition(knownStepperPos);

  this->neckServo.attach(neckServoPin);

  this->lastPhiR = 0;
  this->lastPhiS = 0;
  this->lastPhiD = 0;

  /*
     Giving initial values to the neck transformation matrices.
  */
  this->gCY = KinematicChain::xform(0, 0, 0, 0, (0.0956), (0.0129));
  // should be replaced with actual coordinates from gantry to base of neck
  this->gYN = KinematicChain::xform(0, 0, 0, 0, 0, (0.0672));
  // should be replaced with actual coordinates from base of neck to middle of eyes
  this->gNT = KinematicChain::xform(0, 0, 0, 0, 0, 0.127);

  this->gTC = this->gNT.Inverse() * this->gYN.Inverse() * this->gCY.Inverse();


  // declaring the constant transformation matrices for the neck
  // these transformation matrices will not get updated throughout the program.
  this->gO_B1 = {1.0, 0.0, 0.0, 0.0635 * cos(M_PI_2 + 0 * 2 * M_PI / 3),
                 0.0, 1.0, 0.0, 0.0635 * sin(M_PI_2 + 0 * 2 * M_PI / 3),
                 0.0, 0.0, 1.0, 0.0,
                 0.0, 0.0, 0.0, 1.0
                };
  this->gO_B2 = {1.0, 0.0, 0.0, 0.0635 * cos(M_PI_2 + 2 * 2 * M_PI / 3),
                 0.0, 1.0, 0.0, 0.0635 * sin(M_PI_2 + 2 * 2 * M_PI / 3),
                 0.0, 0.0, 1.0, 0.0,
                 0.0, 0.0, 0.0, 1.0
                };
  this->gO_B3 = {1.0, 0.0, 0.0, 0.0635 * cos(M_PI_2 + 1 * 2 * M_PI / 3),
                 0.0, 1.0, 0.0, 0.0635 * sin(M_PI_2 + 1 * 2 * M_PI / 3),
                 0.0, 0.0, 1.0, 0.0,
                 0.0, 0.0, 0.0, 1.0
                };
  this->gPC_P1 = {1.0, 0.0, 0.0, 0.0635 * cos(M_PI_2 + 0 * 2 * M_PI / 3),
                  0.0, 1.0, 0.0, 0.0635 * sin(M_PI_2 + 0 * 2 * M_PI / 3),
                  0.0, 0.0, 1.0, 0.0,
                  0.0, 0.0, 0.0, 1.0
                 };
  this->gPC_P2 = {1.0, 0.0, 0.0, 0.0635 * cos(M_PI_2 + 2 * 2 * M_PI / 3),
                  0.0, 1.0, 0.0, 0.0635 * sin(M_PI_2 + 2 * 2 * M_PI / 3),
                  0.0, 0.0, 1.0, 0.0,
                  0.0, 0.0, 0.0, 1.0
                 };
  this->gPC_P3 = {1.0, 0.0, 0.0, 0.0635 * cos(M_PI_2 + 1 * 2 * M_PI / 3),
                  0.0, 1.0, 0.0, 0.0635 * sin(M_PI_2 + 1 * 2 * M_PI / 3),
                  0.0, 0.0, 1.0, 0.0,
                  0.0, 0.0, 0.0, 1.0
                 };

  this->gB1_P1 = {0};
  this->gB2_P2 = {0};
  this->gB3_P3 = {0};

  /*
    Length of the spring in meters. Gets updated after MoveToCalState()
    It is 127mm before calibration.
  */
  this->lSpring = 0.127;
}

/*
   Function to calculate the transformation matrices that go from the bottom plate of the neck
   to the top plate of the neck. This function must be called whenever the neck angles are set.
*/
void RobotNeck::updateNeckTransformation()
{
  // getting the matrices that will be raised to the exponent in the next step.
  BLA::Matrix<6> xI01 = {0.0, 0.0, 0.0, 0.0, 0.0, 1.0};
  BLA::Matrix<6> xI12 = {0.0, 0.0, 1.0, this->lastPhiR / this->lSpring, 0.0, 0.0};
  BLA::Matrix<6> xI23 = {0.0, 0.0, 0.0, 0.0, 0.0, 1.0};

  // creating the matrix that will go from the base of the neck to the top of the neck.
  BLA::Matrix<4, 4> g01 = KinematicChain::expmXI(xI01 * this->lastPhiS);
  BLA::Matrix<4, 4> g02 = KinematicChain::expmXI(xI12 * this->lSpring);
  BLA::Matrix<4, 4> g03 = KinematicChain::expmXI(xI23 * -(this->lastPhiS));

  KinematicChain::PrintG(g01);
  KinematicChain::PrintG(g02);
  KinematicChain::PrintG(g03);

  this->gYN = KinematicChain::expmXI(xI01 * this->lastPhiD);
  this->gYN(2, 3) = (0.0672);
  // need to assign the distances once again.
  this->gNT = g01 * g02 * g03;

  this->gB1_P1 = this->gO_B1.Inverse() * this->gNT * this->gPC_P1;
  this->gB2_P2 = this->gO_B2.Inverse() * this->gNT * this->gPC_P2;
  this->gB3_P3 = this->gO_B3.Inverse() * this->gNT * this->gPC_P3;
}

/*
   Returns the inverse transformation matrix that goes from the top of the neck to the center
   of the z axis stepper stage
*/
BLA::Matrix<4, 4> RobotNeck::GetInverseNeckTransformation()
{
  this->gTC = this->gNT.Inverse() * this->gYN.Inverse() * this->gCY.Inverse();
  return this->gTC;
}

/*
   Function to update the neck transformation matrices based on the last PhiR, PhiS and PhiD values.
   The transformation matrices are then used to determine what the current positions of each of the
   neck steppers would be.
*/
void RobotNeck::SetLastNeckPosition()
{
  this->updateNeckTransformation();

  float frontCableLength = sqrt(sq(gB1_P1(0, 3)) + sq(gB1_P1(1, 3)) + sq(gB1_P1(2, 3)));
  float backRightCableLength = sqrt(sq(gB2_P2(0, 3)) + sq(gB2_P2(1, 3)) + sq(gB2_P2(2, 3)));
  float backLeftCableLength = sqrt(sq(gB3_P3(0, 3)) + sq(gB3_P3(1, 3)) + sq(gB3_P3(2, 3)));

  this->m3FrontStepper.SetCurrentPosition(frontCableLength / mmPerStep);

  this->m3BackRightStepper.SetCurrentPosition(backRightCableLength / mmPerStep);

  this->m3BackLeftStepper.SetCurrentPosition(backLeftCableLength / mmPerStep);

  this->neckServo.writeMicroseconds(this->neckServoCenter + this->lastPhiD * (180 / M_PI) * yawMicroSecondsPerDegree);

}

/*
   Function to get the last commanded neck angles based on the string argument passed
   that denotes which angle is to be returned.
*/
float RobotNeck::GetLastNeckPosition(String whichAngle)
{
  if (whichAngle == "PhiR")
  {
    return this->lastPhiR;
  }
  else if (whichAngle == "PhiS")
  {
    return this->lastPhiS;
  }
  else if (whichAngle == "PhiD")
  {
    return this->lastPhiD;
  }
}

/*
   Function to move the neck manually. The function takes in two parameters that determine
   pitch and roll of the neck.
   X and Y should be scaled between -1 and 1.
   Z should be scaled between 0 and 1.
*/
void RobotNeck::MoveNeckManually(float x, float y, float z)
{
  this->lastPhiR = x;
  this->lastPhiS = y;
  this->lastPhiD = z;

  this->updateNeckTransformation();

  float frontCableLength = sqrt(sq(this->gB1_P1(0, 3)) + sq(this->gB1_P1(1, 3)) + sq(this->gB1_P1(2, 3)));
  float backRightCableLength = sqrt(sq(this->gB2_P2(0, 3)) + sq(this->gB2_P2(1, 3)) + sq(this->gB2_P2(2, 3)));
  float backLeftCableLength = sqrt(sq(this->gB3_P3(0, 3)) + sq(this->gB3_P3(1, 3)) + sq(this->gB3_P3(2, 3)));

  this->m3FrontStepper.MoveTo(frontCableLength / mmPerStep);

  this->m3BackRightStepper.MoveTo(backRightCableLength / mmPerStep);

  this->m3BackLeftStepper.MoveTo(backLeftCableLength / mmPerStep);

  this->neckServo.writeMicroseconds(this->neckServoCenter + this->lastPhiD * (180 / M_PI) * yawMicroSecondsPerDegree);
}

/*
   Function to run the stepper motors to the desired set position.
   This function must be called everytime the move neck manually function is called.
*/
void RobotNeck::RunSteppers()
{
  unsigned long startTime = micros();
  unsigned long frontNext = startTime + ((1L * 1000L * 1000L) / this->m3FrontStepper.GetSpeed());
  unsigned long backRightNext = startTime + ((1L * 1000L * 1000L) / this->m3BackRightStepper.GetSpeed());
  unsigned long backLeftNext = startTime + ((1L * 1000L * 1000L) / this->m3BackLeftStepper.GetSpeed());

  while (!(m3FrontStepper.IsReached()) || !(m3BackRightStepper.IsReached()) || !(m3BackLeftStepper.IsReached()))
  {
    unsigned long currentTime = micros();

    if (currentTime >= frontNext)
    {
      this->m3FrontStepper.RunStepper();

      //SerialTerminal->print("front: ");
      Serial.println(this->m3FrontStepper.CurrentPosition());
      frontNext = currentTime + ((1L * 1000L * 1000L) / this->m3FrontStepper.GetSpeed());
    }
    if (currentTime >= backRightNext)
    {
      this->m3BackRightStepper.RunStepper();

      //SerialTerminal->print("Right: ");
      Serial.println(this->m3BackRightStepper.CurrentPosition());
      backRightNext = currentTime + ((1L * 1000L * 1000L) / this->m3BackRightStepper.GetSpeed());
    }
    if (currentTime >= backLeftNext)
    {
      this->m3BackLeftStepper.RunStepper();

      //SerialTerminal->print("left: ");
      Serial.println(this->m3BackLeftStepper.CurrentPosition());
      backLeftNext = currentTime + ((1L * 1000L * 1000L) / this->m3BackLeftStepper.GetSpeed());
    }
  }
}

/*
   Function to write the current neck stepper positions to the EEPROM.
   This function can save the positions to either the calibration variables in the PROM
   or the last stepper position variables in the PROM based on the character input.
   'c' for calibration. 'l' for last stepper.
*/
void RobotNeck::WriteNeckPositionToProm()
{
  PromAddress eeAddress = LastPhiR;

  Serial.println(this->lastPhiR);
  EEPROM.put(eeAddress, this->lastPhiR);
  eeAddress = (PromAddress)((int)eeAddress + 4);

  Serial.println(this->lastPhiS);
  EEPROM.put(eeAddress, this->lastPhiS);
  eeAddress = (PromAddress)((int)eeAddress + 4);

  EEPROM.put(eeAddress, this->lastPhiD);
  eeAddress = (PromAddress)((int)eeAddress + 4);

  EEPROM.put(eeAddress, this->neckServoCenter);
  delay(100);

  //SerialTerminal->println("Neck variables written!");
}

/*
   Function to read either the calibration stepper positions
   or the last neck stepper positions from the EEPROM. The character input into the function
   determines which variables are read.
*/
void RobotNeck::ReadNeckPositionFromProm()
{
  PromAddress eeAddress = LastPhiR;
  float angle = 0.0;
  long int stepperPosition = 0;

  // reading last commanded PhiR, PhiS, PhiD values
  EEPROM.get(eeAddress, angle);
  this->lastPhiR = angle;
  Serial.println(this->lastPhiR);
  eeAddress = (PromAddress)((int)eeAddress + 4);

  EEPROM.get(eeAddress, angle);
  this->lastPhiS = angle;
  eeAddress = (PromAddress)((int)eeAddress + 4);

  EEPROM.get(eeAddress, angle);
  this->lastPhiD = angle;
  eeAddress = (PromAddress)((int)eeAddress + 4);

  // reading neck servo center location and sending to center.
  EEPROM.get(eeAddress, stepperPosition);
  this->neckServoCenter = stepperPosition;

  //SerialTerminal->println("Neck variables read!");
}
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

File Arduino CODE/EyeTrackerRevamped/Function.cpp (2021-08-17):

/*
   This source file contains declarations for all extern variables
   declared in the header file.
*/

#include "Function.h"

Adafruit_BNO055 bno = Adafruit_BNO055(55);

HardwareSerial *SerialTerminal = &Serial1;

// Initialize XBOX and USB Objects
USB Usb;
XBOXONE Xbox(&Usb);

// String array containing state names corresponding
// to enumeration.
String stateNames[12] = {"MenuMode", "ServoCalibration", "Auto", "StepperHome", "StepperManual", "FindCoordinates",
                         "SetCoordinates", "ServoManual", "NeckCalibration", "MoveToCalibrationState", "Neck", "SpinnyBoi"
                        };

// Declare Servo Pins - check wiring diagram if you have any questions
int xLPin = 11;
int zLPin = 5;
int xRPin = 6;
int zRPin = 3;

//Declaring Servo relay pin
int servoRelay = 8;

// Declaring Shoulder Limit Switches and Stepper Pins - check wiring diagram if you have any questions
// Limit switch pins
int xEnd = 2; // X axis limit switch pin
int zEnd = 4; // Z axis limit switch pin
int yEnd = 7; // Y axis limit switch pin
// SHOULDER Stepper Direction and Pulse Pins
int xDir = A1;
int xPulse = A0;
int yDir = A3;
int yPulse = A2;
int zDir = A5;
int zPulse = A4;

// Declaring Neck stepper Direction and Pulse pins.
int frontDir = 40; 
int frontPulse = 42; 
int backRightDir = 44; 
int backRightPulse = 46; 
int backLeftDir = 48;  
int backLeftPulse = 14; //50 on PCB; but 50 is unusable so connection has been by-passed.
// Declaring neck servo pins
int neckServoPin = 12;

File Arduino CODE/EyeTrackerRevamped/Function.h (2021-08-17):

/*
   This is the header file that is being used to store the global variables,
   configuration variables, kinematic chain map object and EEPROM logger object.
   These objects and variables are used by almost all the other files and hence
   are stored here.
*/
#ifndef _FUNCTION_H
#define _FUNCTION_H

#include <XBOXONE.h>
// Including the libraries for the IMU - acclerometer
#include <Adafruit_Sensor.h>
#include <Adafruit_BNO055.h>
#include <utility/imumaths.h>

// Including library for the matrix elements in the code
#include <BasicLinearAlgebra.h>

#include <AccelStepper.h>
#include <EEPROM.h>

// state machine enumeration.
enum StateMachineState {
  MenuMode = 0,
  RobotRun = 1,
  EyeCalibrate = 2,
  NeckCalibrate = 3,
  ShoulderCalibrate = 4,
};

// EEPROM address enumeration.
enum PromAddress {
  LXCenter = 12,
  LZCenter = 16,
  RXCenter = 20,
  RZCenter = 24,
  XStepperPosition = 0,
  YStepperPosition = 4,
  ZStepperPosition = 8,
  LastPhiR = 28,
  LastPhiS = 32,
  LastPhiD = 36,
  YawServoCalibrationCenter = 40,
};

// declaring global variables as extern. They are declared
// in the source file for this header.

// BNO IMU object
extern Adafruit_BNO055 bno;

// Hardware Serial object for comms with API
// Hardware Serial is just a pointer to Serial1.
extern HardwareSerial *SerialTerminal;

// XBOX and USB objects
extern USB Usb;
extern XBOXONE Xbox;

// String array containing the state names.
extern String stateNames[12];

// Declare Servo Pins - check wiring diagram if you have any questions
extern int xLPin;
extern int zLPin;
extern int xRPin;
extern int zRPin;

// Declaring Servo Relat Pin
extern int servoRelay;
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

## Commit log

2021-03-29 Add 2020 Team Project files
    [.25in Angle Bracket.SLDPRT, 1010 X.SLDPRT, 1010 Y End Piece.SLDPRT, 1010 Y.SLDPRT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]
2021-04-24 Create ME416-Spring 2021
2021-05-10 First commit with all the artifacts from Jan-May 2021 semester
    [47065T236_ALUMINUM T-SLOTTED FRAMING EXTRUSION.SLDPRT, 5031T133_BALL-GRIP POSITIONING ARM.SLDPRT, 6495K230_TIMING BELT PULLEY.SLDPRT, 7010K142_WALL-MOUNT TRANS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]
2021-05-10 Initial commit with all the artifacts of MASCOT and SPARKS teams
    [47065T236_ALUMINUM T-SLOTTED FRAMING EXTRUSION.SLDPRT, 5031T133_BALL-GRIP POSITIONING ARM.SLDPRT, 6495K230_TIMING BELT PULLEY.SLDPRT, 7010K142_WALL-MOUNT TRANS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]
2021-05-10 Commiting wiring diagrams
    [WSU ME416 Wiring PCB FINAL.dwg]
2021-05-10 Commiting python script for auto functionality of robot.
    [Eyetracker_Keyboard.csv]
2021-07-16 Commiting changes made to Shoulder.cpp for homing and moving steppers.
2021-08-10 Commiting M3 stepper implementation for improved neck stepper motion. Changes made to kinematic chain class to improve gaze parallax.
2021-08-11 Imported in updated Control Application files. Reorder GitHub files.
    [.25in Angle Bracket.SLDPRT, 1010 X.SLDPRT, 1010 Y End Piece.SLDPRT, 1010 Y.SLDPRT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]
